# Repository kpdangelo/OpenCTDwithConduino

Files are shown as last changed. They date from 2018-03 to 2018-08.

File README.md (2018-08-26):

# OpenCTDwithConduino
OpenCTD with a low cost Conduino conductivity sensor

This has drift issues, see https://github.com/kpdangelo/OpenCTD-Conduino-K1.0 

*********************************************************************************************************************************************
This version is the basic design. During testing, a major drift in the reading was discovered. Two revisions were made, with some improvement. Continuing research is being done on Version 3 - see a separate entry for that, OpenCTDwithConduinoV3.
*********************************************************************************************************************************************

This project merges the Oceanography for Everyone Open CTD with the Conduino conductivity sensor.

Open CTD:
https://github.com/OceanographyforEveryone/OpenCTD

Conduino:
Marco Carminati, Paolo Luzzatto-Fegiz,
Conduino: Affordable and high-resolution multichannel water conductivity sensor using micro USB connectors,
In Sensors and Actuators B: Chemical, Volume 251, 2017, Pages 1034-1041, ISSN 0925-4005,
https://doi.org/10.1016/j.snb.2017.05.184.

Follow the basic assembly instructions from OpenCTD along with the included instructions for constructing
a Conduino.

PCBs can be ordered from OSHPARK, or Eagle and Gerber files are included here.

The system goes into a 2" PVC pipe and seals with Marine Epoxy and a 3D printed plug (file included here). 
See Conduino Pipe Assembly.pdf file.

First test was taking it into the surf and turbulence here at Spanish Bay for a few minutes, see excel file for that gem.

March 25, 2018

3/27/18
slight modification to the schematic to take away the filter on the network analyzer buffer (C5 and R3). It was giving a gigantic time constant to the measurement.

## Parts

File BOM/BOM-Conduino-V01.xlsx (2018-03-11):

Conduino Partslist
PCB can be ordered directly from OSHPARK
Part | Value | Device | Package | Description | Cost (single) | link
C1 | 1uF | CAP0603-CAP | 0603-CAP | Capacitor | $0.22 | https://www.digikey.com/product-detail/en/murata-electronics-north-america/GRM21BR61E106KA73L/490-5523-1-ND/2334919
C4 | 1uF | CAP0603-CAP | 0603-CAP | Capacitor | $0.22
C5 | 10pF | CAP0603-CAP | 0603-CAP | Capacitor | $0.29 | https://www.digikey.com/product-detail/en/kemet/C0603C100J8GAC7867/399-14932-1-ND/7382481
C8 | 100nF | CAP0603-CAP | 0603-CAP | Capacitor | $0.38 | https://www.digikey.com/product-detail/en/avx-corporation/08051C104JAT2A/478-5780-1-ND/2136372
C9 | 10uF | CAP0603-CAP | 0603-CAP | Capacitor | $0.15 | https://www.digikey.com/product-detail/en/taiyo-yuden/LMK212BJ106KG-T/587-1300-1-ND/931077
C10 | 100nF | CAP0603-CAP | 0603-CAP | Capacitor | $0.38
C11 | 1uF | CAP0603-CAP | 0603-CAP | Capacitor | $0.22
C12 | 10uF | CAP0603-CAP | 0603-CAP | Capacitor | $0.15
C13 | 100nF | CAP0603-CAP | 0603-CAP | Capacitor | $0.38
C16 | 10uF | CAP0603-CAP | 0603-CAP | Capacitor | $0.15
C17 | 100nF | CAP0603-CAP | 0603-CAP | Capacitor | $0.38
J1 | USBA-SIDE | USBA-SIDE | USBA-SIDE | USB Port | $0.40 | https://www.digikey.com/product-detail/en/amphenol-commercial-products/UE27AC54100/UE27AC54100-ND/1972253
J2 | Connector | 1X04 Header |  | Connector |  | use 0.1 mil headers
J3 | Connector | 1X02 header |  | Connector
R3 | 150K | RESISTOR0603-RES | 0603-RES | 0.10% | $0.35 | https://www.digikey.com/product-detail/en/panasonic-electronic-components/ERA-3AEB154V/P150KDBCT-ND/1466104
R4 | 20K | RESISTOR0603-RES | 0603-RES | 0.10% | $0.39 | https://www.digikey.com/product-detail/en/yageo/RT0805BRD0720KL/YAG1823CT-ND/5139271
R7 | 180 | RESISTOR0603-RES | 0603-RES | 0.10% | $0.35 | https://www.digikey.com/product-detail/en/panasonic-electronic-components/ERA-3AEB181V/P180DBCT-ND/1466034
R9 | 1.6K | RESISTOR0603-RES | 0603-RES | 1% | $0.10 | https://www.digikey.com/product-detail/en/panasonic-electronic-components/ERJ-3EKF1601V/P1.60KHCT-ND/1746732
R10 | 20K | RESISTOR0603-RES | 0603-RES | 0.10% | $0.39
U1 | AD5933SSOP-16-AD | AD5933SSOP-16-AD | SSOP-16-AD | Network Analyzer | $36.32 | https://www.digikey.com/product-detail/en/analog-devices-inc/AD5933YRSZ/AD5933YRSZ-ND/756602
U2 | AD4891-2 | AD4891-2 | SOIC_N | Op Amps | $2.09 | https://www.digikey.com/product-detail/en/analog-devices-inc/ADA4891-2ARZ/ADA4891-2ARZ-ND/2342638
U3 | ADR440A | ADR440A | SOIC_N | Voltage Reference | $6.32 | https://www.digikey.com/product-detail/en/analog-devices-inc/ADR440ARZ/ADR440ARZ-ND/1218276
PCB |  |  |  | Conduino PCB | $1.40 | https://www.oshpark.com/shared_projects/yAFaZZxk
 |  |  |  |  | $51.03

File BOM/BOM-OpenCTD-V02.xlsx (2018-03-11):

Open CTD with Conduino Partslist
Part | Value | Device | Package | Description | Cost (single)
JP1 | M031X03_NO_SILK | 1X03_NO_SILK | Header | Temp Sensor
JP2 | M031X03_NO_SILK | 1X03_NO_SILK | Header | Temp Sensor
JP3 | M031X03_NO_SILK | 1X03_NO_SILK | Header | Temp Sensor
JP4 | M041X04_NO_SILK | 1X04_NO_SILK | Header | Pressure Sensor
R1 | 4.7K | RESISTORPTH-1/4W | AXIAL-0.4 | Resistor
U1 | QDUINO_MINI | QDUINO_MINI | QDUINO_MINI |  | $29.95 | https://www.sparkfun.com/search/results?term=qduino
U2 | CONDUINO-V01 | CONDUINO-V01 | CONDUINO-V01 |  | $51.03
U3 | SD-CARD-READER-MICRO | SD-CARD-READER-MICRO | MICROSD_MOLEX |  | $1.11 | https://www.digikey.com/product-detail/en/molex-llc/0472192001/WM6698CT-ND/3044147
 | 12-position header for Qduino |  |  |  | $0.81 | https://www.digikey.com/product-detail/en/sullins-connector-solutions/PPPC121LFBN-RC/S7045-ND/810184
 | 12-position header for Qduino |  |  |  | $0.81
 | 4-position header for Conduino |  |  |  | $0.47 | https://www.digikey.com/product-detail/en/sullins-connector-solutions/PPPC041LFBN-RC/S7037-ND/810176
 | 2-position header for Conduino |  |  |  | $0.33 | https://www.digikey.com/product-detail/en/sullins-connector-solutions/PPPC021LFBN-RC/S7035-ND/810174
 | Pressure Sensor |  |  |  | $16.58 | https://www.digikey.com/product-detail/en/te-connectivity-measurement-specialties/MS580314BA01-00/223-1626-5-ND/5277631
 | 3 temperature sensors |  |  |  | $8.98 | https://www.amazon.com/gp/product/B00Q9YBIJI/ref=oh_aui_search_detailpage?ie=UTF8&psc=1
 | PCB | order from OSHPARK 3 at a time ($24.80) |  |  | $8.26 | https://www.oshpark.com/shared_projects/Nnyqy5C8
 | 2 Ah battery |  |  |  | $17.41 | https://www.amazon.com/gp/product/B0137ITW46/ref=oh_aui_search_detailpage?ie=UTF8&psc=1
 | PCB for pressure sensor |  |  |  | $2.95 | https://www.sparkfun.com/products/13655
 |  |  |  |  | $138.69

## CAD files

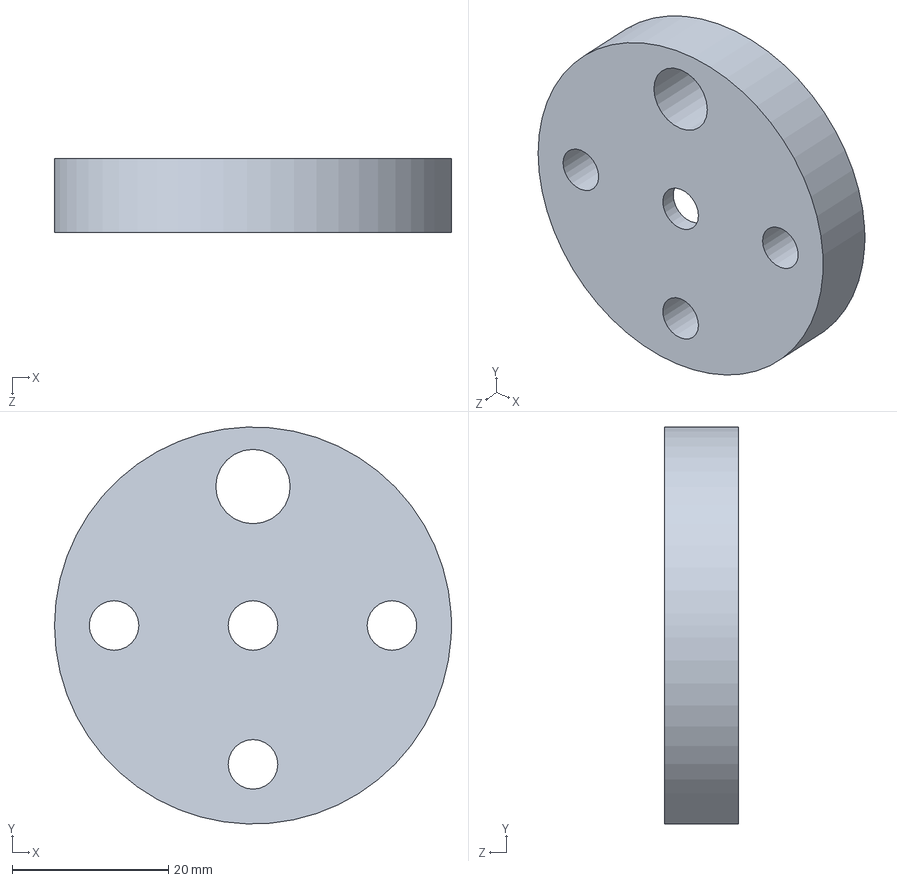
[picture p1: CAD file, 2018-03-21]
3D_Printer_Files/OpenCTD-Conduino-EndPlug.SLDPRT
50.8 x 50.8 x 9.53 mm

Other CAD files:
3D_Printer_Files/OpenCTD-Conduino-EndPlug.STL

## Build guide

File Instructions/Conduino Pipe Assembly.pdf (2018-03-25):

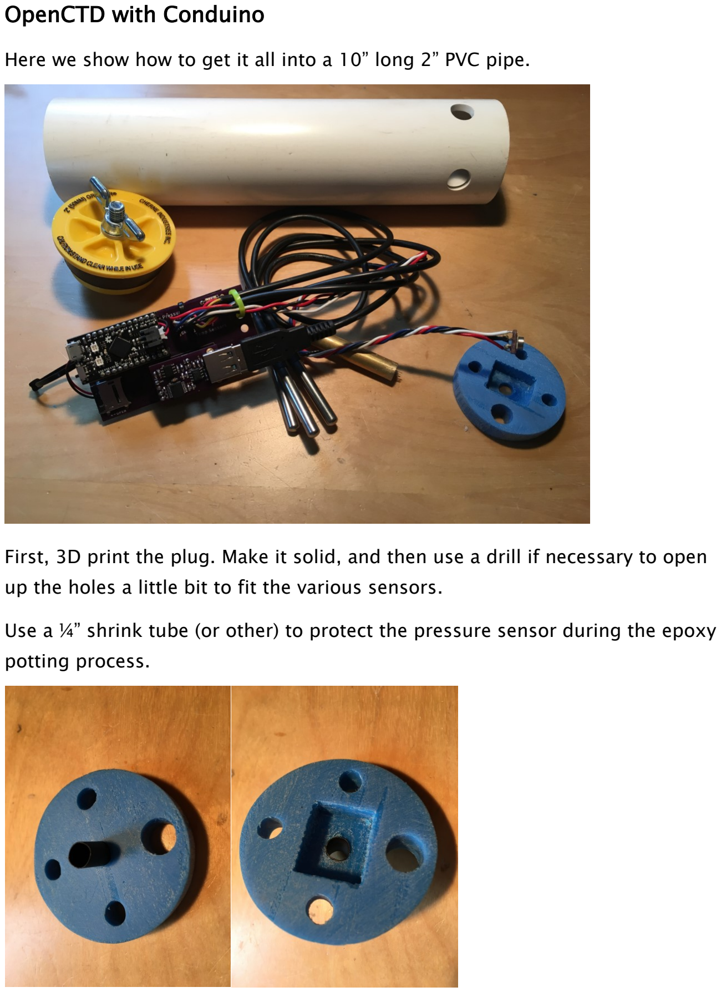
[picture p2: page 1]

OpenCTD with Conduino

Here we show how to get it all into a 10” long 2” PVC pipe.

First, 3D print the plug. Make it solid, and then use a drill if necessary to open up the holes a little bit to fit the various sensors.

Use a ¼” shrink tube (or other) to protect the pressure sensor during the epoxy potting process.

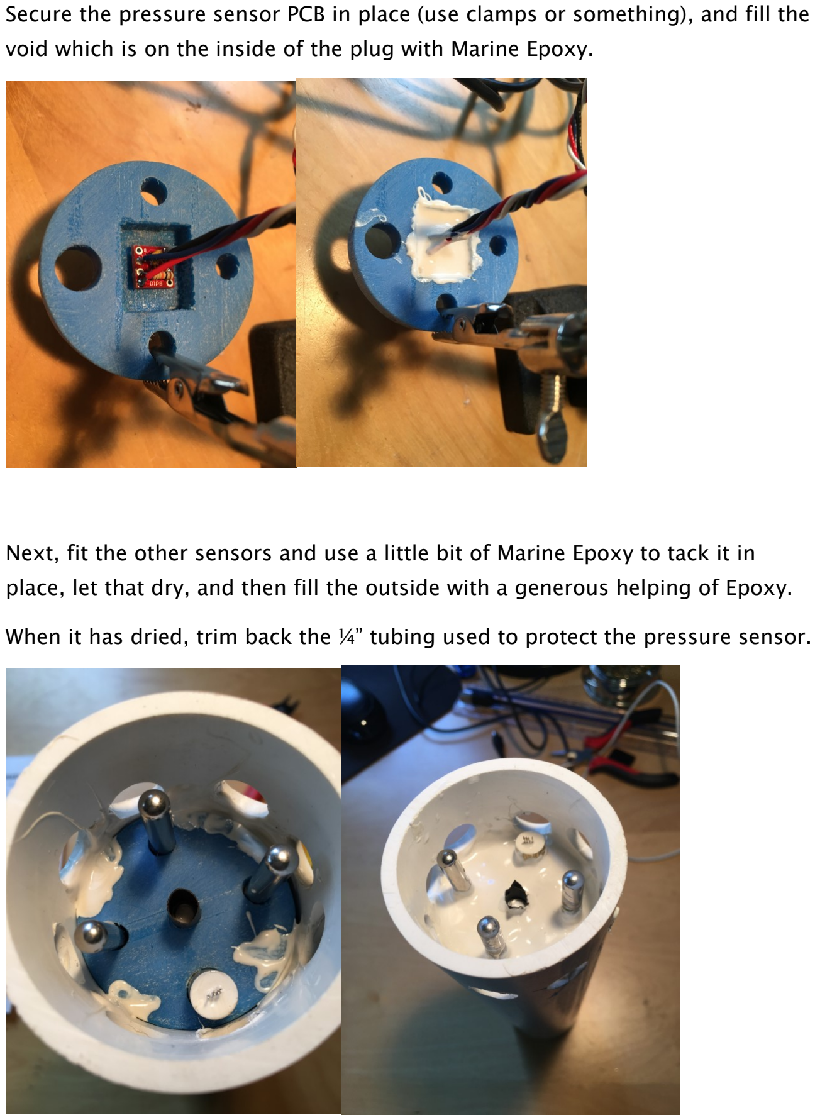
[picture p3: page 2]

Secure the pressure sensor PCB in place (use clamps or something), and fill the void which is on the inside of the plug with Marine Epoxy.

Next, fit the other sensors and use a little bit of Marine Epoxy to tack it in place, let that dry, and then fill the outside with a generous helping of Epoxy.

When it has dried, trim back the ¼” tubing used to protect the pressure sensor.

Cram the circuit board and the wires in the pipe. A twist of the circuit board is helpful. Attach the Gripper Plug and you’re ready to go. If you need it to sink, fill with mineral oil, or attach a weight.

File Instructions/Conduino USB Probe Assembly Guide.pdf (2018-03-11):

OpenCTD with Conduino

This version of the Open CTD instrument utilizes a Conduino conductivity probe made from a micro-USB cable.

https://github.com/OceanographyforEveryone/OpenCTD

Here’s a photo of the Conduino with three temperature sensors and calibration curve:

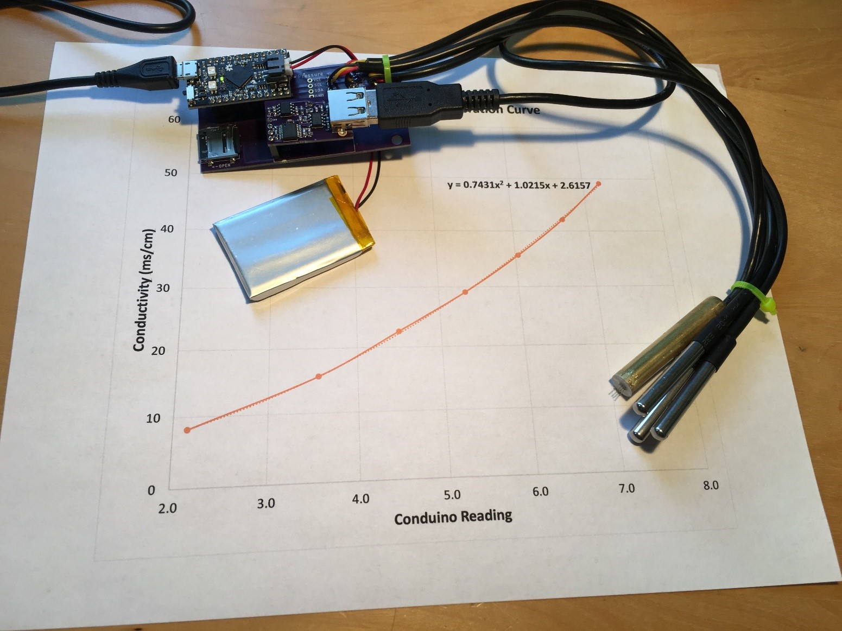
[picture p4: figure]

Conduino USB Probe Assembly Guide

Here’s one way to convert a micro-USB connector to a Conduino probe. Be patient and go slowly with the X-ACTO knife so the cable connections are preserved. A microscope is helpful.

First strip off the end of the cable housing by making a cut on all four sides.

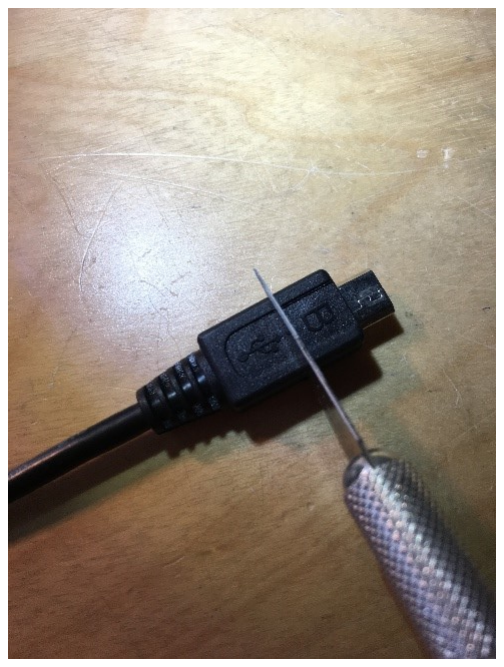
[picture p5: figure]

Cut again into fourths for ease of removal.

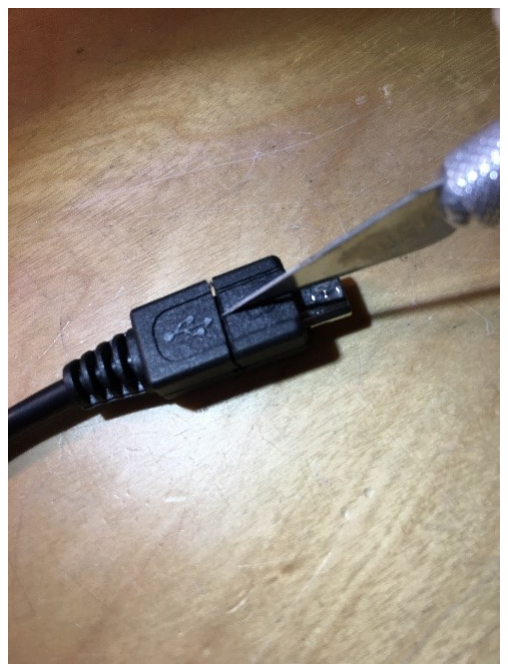
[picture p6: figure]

Remove the end of the housing and expose the connector.

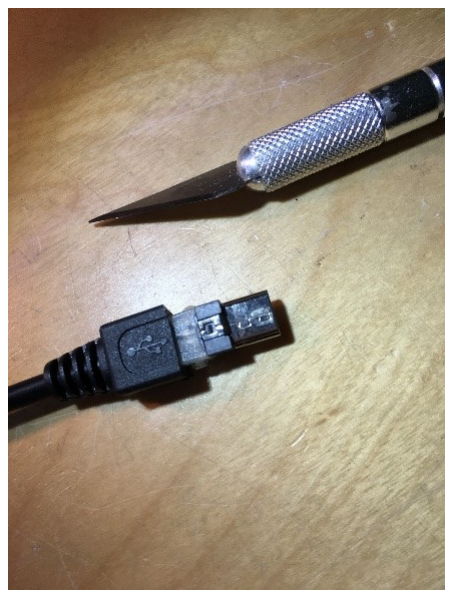
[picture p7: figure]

Peel back the clips on the four sides.

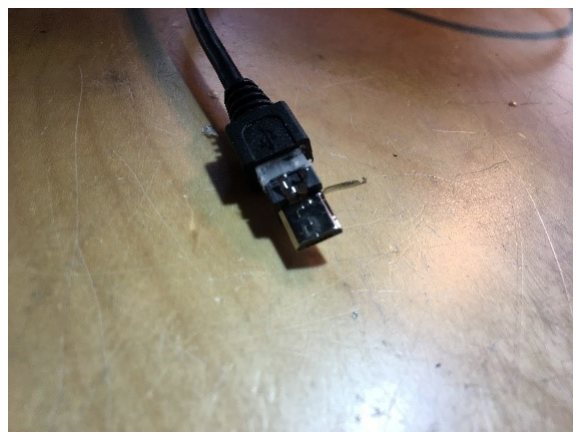
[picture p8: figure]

Carefully pull off the connector to reveal the electrodes. Darn, one of the electrodes came undone. Fortunately it’s the ID pin which is unused. The Conduino board uses D+ and D-.

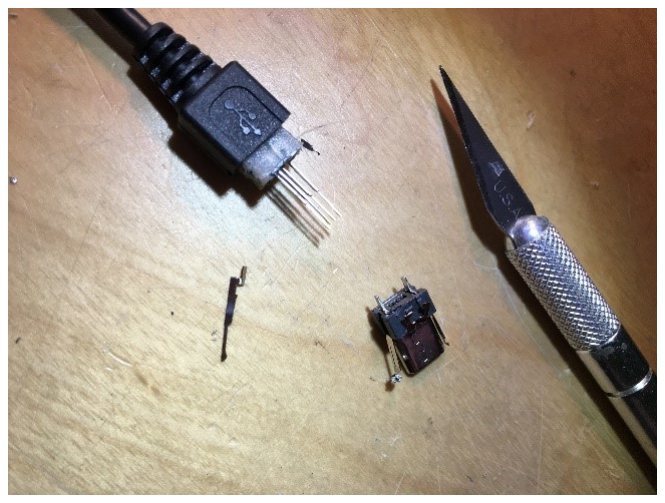
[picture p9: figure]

Now get rid of the rest of the housing so it can fit into a tube. Again, divide the housing into fourths by cutting down and slicing with the X-ACTO knife. Here’s all of the discarded stuff along with what remains of the cable we’ll use.

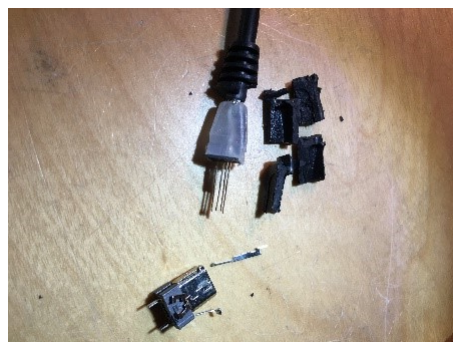
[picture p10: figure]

Use Marine Epoxy, readily available at Home Depot to cement the probe into a 3/8” tube. This tube is a brass tube because that’s what the local hardware store had.

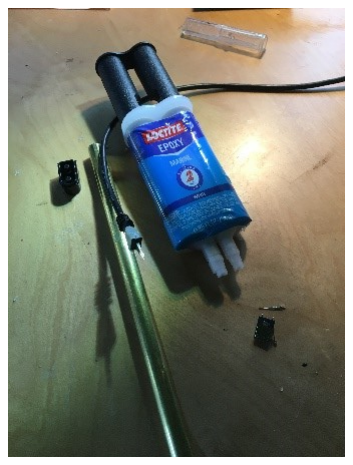
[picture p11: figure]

Use a holder to support the assembly while filling the void with epoxy. Here a Q-tip is used to mix and transport the epoxy.

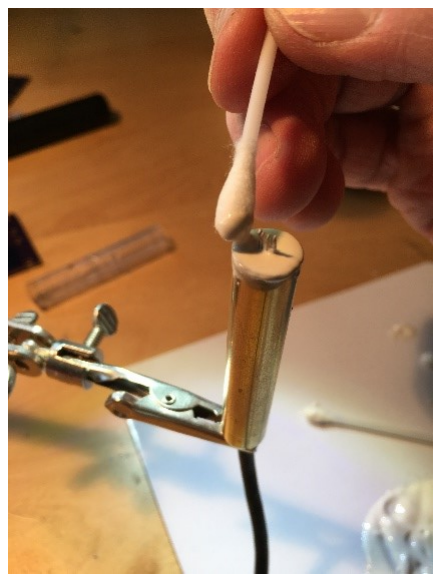
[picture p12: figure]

Use the X-ACTO knife to carefully clear away the excess stuck to the electrodes now. In about an hour after the epoxy has set, use a microscope and knife to clear away all of the excess epoxy. Then allow 24 hours or so to fully cure.

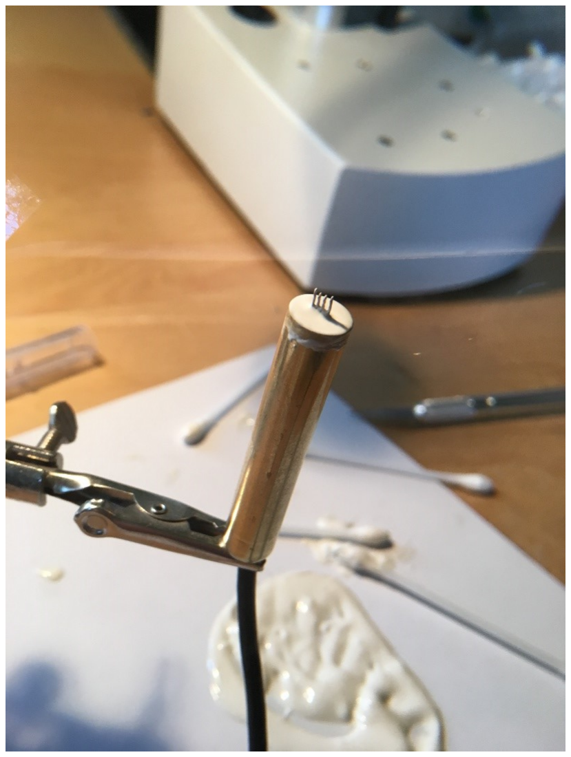
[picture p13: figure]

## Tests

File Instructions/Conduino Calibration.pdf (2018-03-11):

Conduino Calibration

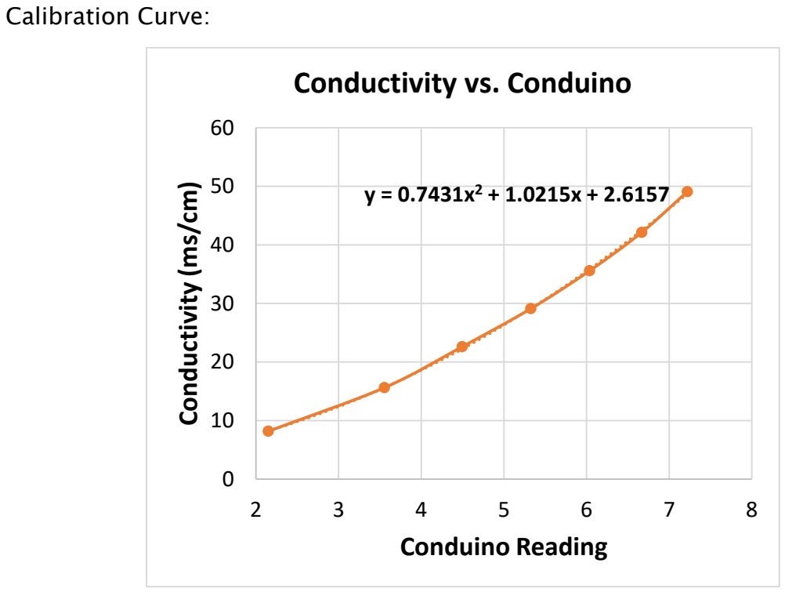
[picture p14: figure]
Calibration Curve:; Conductivity (ms/cm); Conduino Reading; Conductivity vs. Conduino

Seven known salinity samples were used to generate this curve: 5, 10, 15, 20, 25, 30 and 35 ppt salt concentration. To make the samples, weigh out half of the intended salt concentration (e.g. 2.5g, 5g, 7.5g etc.) and then add water to make the total weight 500g (or if you have a big vessel, go up to 1000g with the full salt weight).

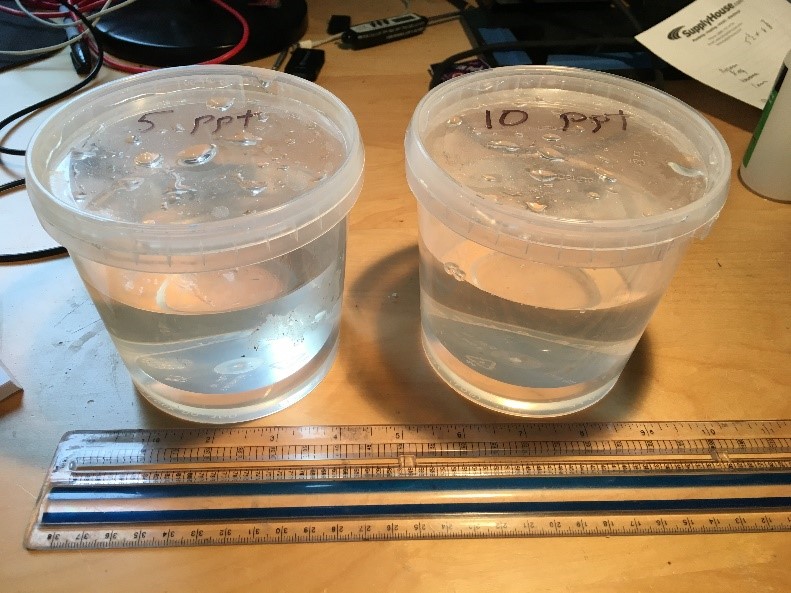
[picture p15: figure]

To take calibration measurements, use a temperature sensor along with the Conduino. Here, three temperature sensors were attached to the Conduino to be averaged during calibration. While constantly stirring the solution with the Conduino/Temperature sensor bundle, run the Arduino sketch and write the sensor values to the Arduino serial monitor. When the readings stabilize, cut a chunk of data and paste it into a txt file, and then import the txt file into Excel for averaging.

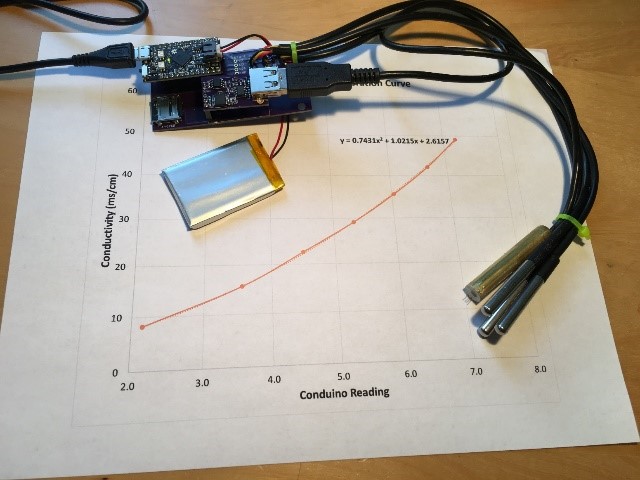
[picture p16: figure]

Use an online calculator to calculate a conductivity value based on temperature (sensed) and concentration (known):

http://salinometry.com/stp-conductivity-calculator/

Plot the data points for the 7 known samples as Conductivity vs. Conduino Reading. Add a trendline, in this case a polynomial, and add that to the sketch, or use it in a salinity calculating spreadsheet.

Data Sample:

Salinity (PPT) | t1 | t2 | t3 | Conduino Reading | Conductivity from salinometry.com | T average
5 | 20.56 | 20.60 | 20.62 | 2.150 | 8.171 | 20.59
10 | 20.75 | 20.81 | 20.87 | 3.554 | 15.608 | 20.81
15 | 20.65 | 20.69 | 20.75 | 4.494 | 22.598 | 20.70
20 | 20.23 | 20.25 | 20.31 | 5.326 | 29.100 | 20.26
25 | 20.14 | 20.19 | 20.25 | 6.036 | 35.572 | 20.19
30 | 20.37 | 20.44 | 20.45 | 6.667 | 42.122 | 20.42
35 | 21.12 | 21.15 | 21.19 | 7.220 | 49.090 | 21.15

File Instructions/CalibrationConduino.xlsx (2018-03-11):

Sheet: Sheet1
 | Conductivity calculators:
 | http://www.fivecreeks.org/monitor/sal.shtml
 | http://salinometry.com/stp-conductivity-calculator/
 | Polynomial Coefficients
 | 0.7431
 | 1.0215
 | 2.6157
data taken while constantly stirring known solutions
Salinity (PPT) | t1 | t2 | t3 | Conduino | ppt known Solutions | Conductivity from salinometry.com | T average | t1 | t2 | t3 | Conductivity polynomial calculation | *1000 | Salinity ppt calculated | Error
5 | 20.56 | 20.60 | 20.62 | 2.150 | 5 | 8.171 | 20.59 | 20.56 | 20.60 | 20.62 | 8.247 | 8247.087481 | 5.05 | 1.04%
10 | 20.75 | 20.81 | 20.87 | 3.554 | 10 | 15.608 | 20.81 | 20.75 | 20.81 | 20.87 | 15.630 | 15629.79149 | 10.02 | 0.20%
15 | 20.65 | 20.69 | 20.75 | 4.494 | 15 | 22.598 | 20.70 | 20.65 | 20.69 | 20.75 | 22.212 | 22212.3194 | 14.73 | -1.81%
20 | 20.23 | 20.25 | 20.31 | 5.326 | 20 | 29.100 | 20.26 | 20.23 | 20.25 | 20.31 | 29.135 | 29135.02113 | 20.03 | 0.16%
25 | 20.14 | 20.19 | 20.25 | 6.036 | 25 | 35.572 | 20.19 | 20.14 | 20.19 | 20.25 | 35.860 | 35859.64658 | 25.23 | 0.94%
30 | 20.37 | 20.44 | 20.45 | 6.667 | 30 | 42.122 | 20.42 | 20.37 | 20.44 | 20.45 | 42.455 | 42454.98524 | 30.28 | 0.93%
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

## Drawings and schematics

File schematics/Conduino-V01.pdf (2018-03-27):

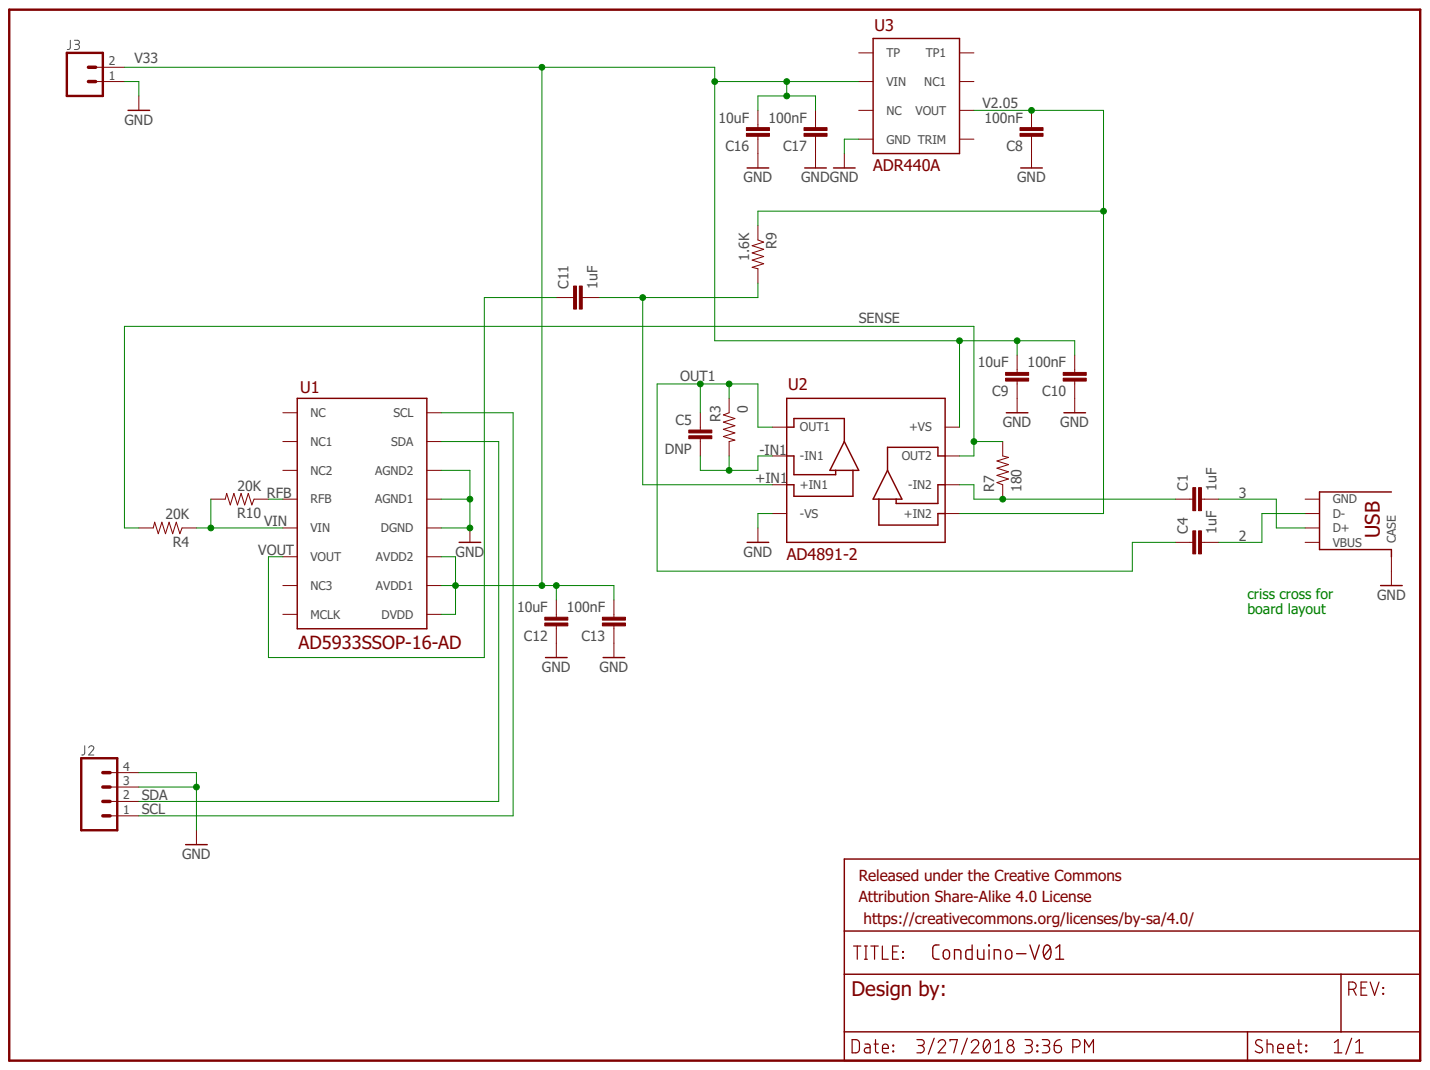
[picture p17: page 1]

criss cross for board layout

Released under the Creative Commons Attribution Share-Alike 4.0 License https://creativecommons.org/licenses/by-sa/4.0/

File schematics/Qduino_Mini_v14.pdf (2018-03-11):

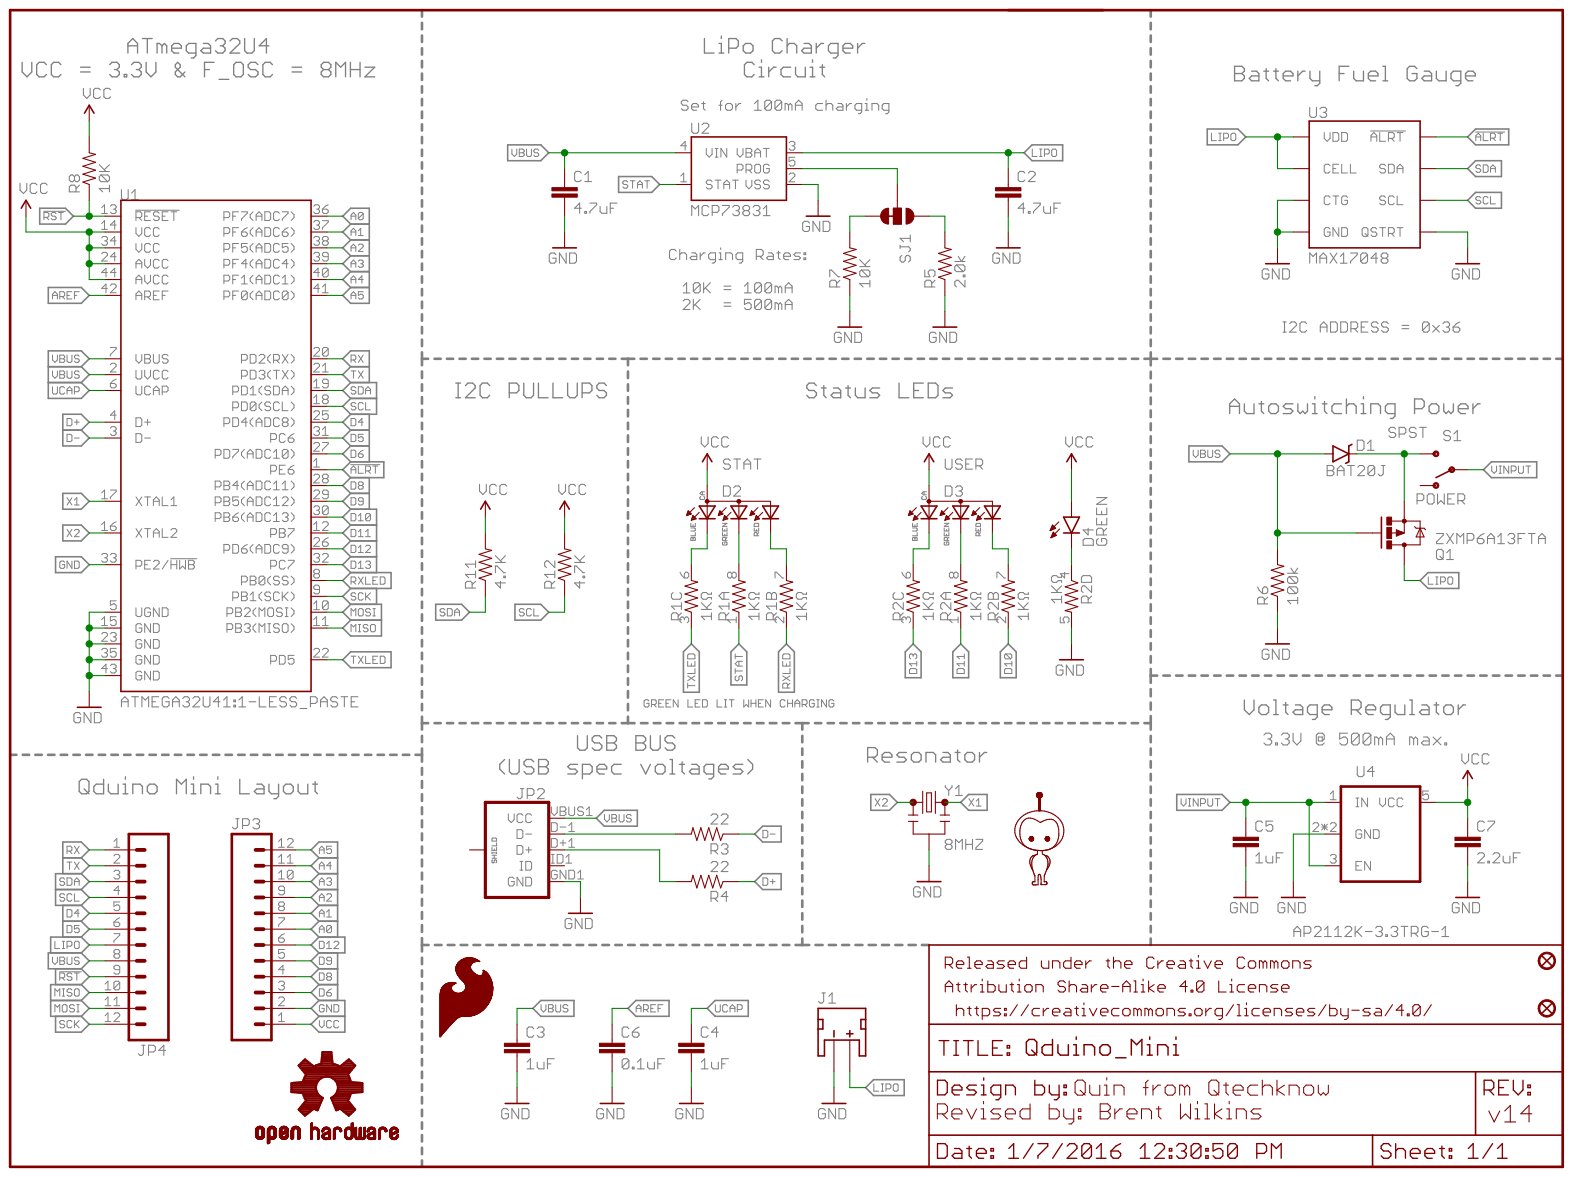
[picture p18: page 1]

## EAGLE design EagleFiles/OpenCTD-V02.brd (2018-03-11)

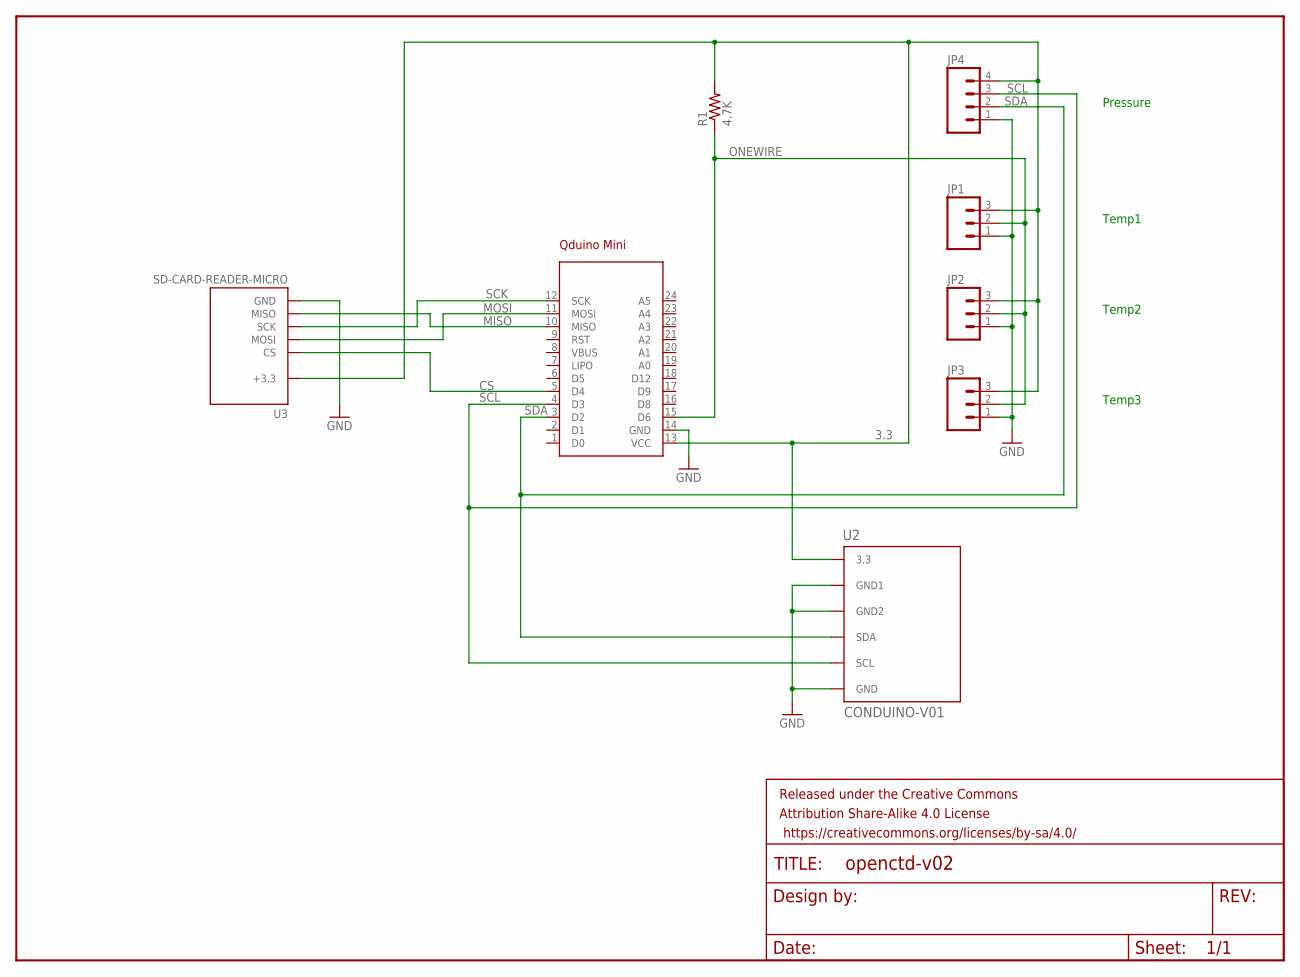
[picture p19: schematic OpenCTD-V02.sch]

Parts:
FRAME1: FRAME-LETTER; CREATIVE_COMMONS
JP1, JP2, JP3: M031X03_NO_SILK; 1X03_NO_SILK
JP4: M041X04_NO_SILK; 1X04_NO_SILK
R1: 4.7K; AXIAL-0.4
U1: QDUINO_MINI
U2: CONDUINO-V01
U3: SD-CARD-READER-MICRO; MICROSD_MOLEX

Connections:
3.3: JP1.3, JP2.3, JP3.3, JP4.4, R1.P$2 (2), U1.13 (VCC), U2.6 (3.3), U3.P$4 (+3.3)
CS: U1.5 (D4), U3.P$2 (CS)
GND: JP1.1, JP2.1, JP3.1, JP4.1, U1.14 (GND), U2.3 (GND), U2.4 (GND1), U2.5 (GND2), U3.P$6 (GND), U3.P$9 (GND), U3.P$10 (GND), U3.P$11 (GND), U3.P$12 (GND)
MISO: U1.10 (MISO), U3.P$7 (MISO)
MOSI: U1.11 (MOSI), U3.P$3 (MOSI)
ONEWIRE: JP1.2, JP2.2, JP3.2, R1.P$1 (1), U1.15 (D6)
SCK: U1.12 (SCK), U3.P$5 (SCK)
SCL: JP4.3, U1.4 (D3), U2.1 (SCL)
SDA: JP4.2, U1.3 (D2), U2.2 (SDA)

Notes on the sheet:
Pressure
Temp1
Temp2
Temp3

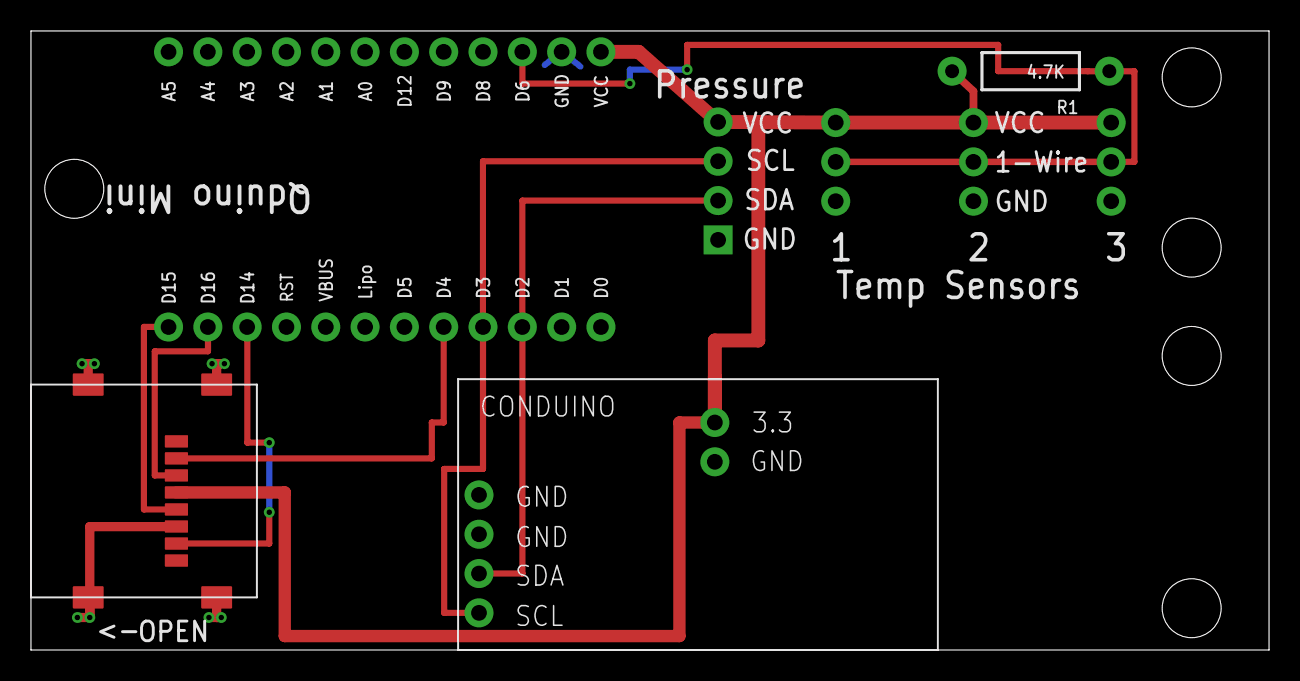
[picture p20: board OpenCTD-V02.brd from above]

Board: 2 copper layers, 80.0 x 40.0 mm, 9 parts (0 on the bottom side), 9 nets.

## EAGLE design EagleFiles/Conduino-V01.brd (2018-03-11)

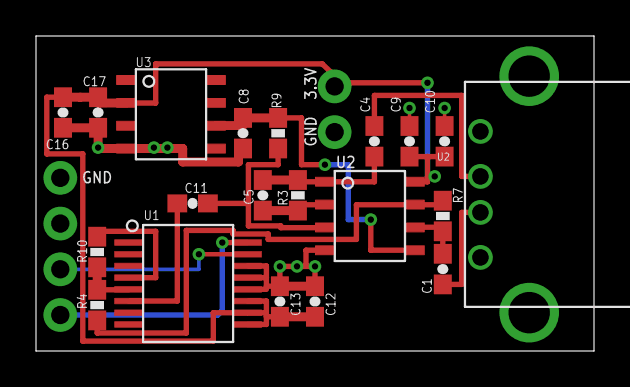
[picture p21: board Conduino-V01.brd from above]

Board: 2 copper layers, 31.0 x 17.5 mm, 23 parts (0 on the bottom side), 15 nets.

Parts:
C1, C4, C11: 1uF; 0603-CAP
C5: 10pF; 0603-CAP
C8, C10, C13, C17: 100nF; 0603-CAP
C9, C12, C16: 10uF; 0603-CAP
FRAME1: FRAME-LETTER; CREATIVE_COMMONS
J1: USBA-SIDE
J2: 1X04_NO_SILK
J3: 1X02_NO_SILK
R3: 150K; 0603-RES
R4, R10: 20K; 0603-RES
R7: 180; 0603-RES
R9: 1.6K; 0603-RES
U1: AD5933SSOP-16-AD; SSOP-16-AD
U2: AD4891-2; SOIC_N
U3: ADR440A; SOIC_N

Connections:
2: C4.2, J1.P$2
3: C1.2, J1.P$3
+IN1: C11.2, R9.2, U2.P$3
-IN1: C5.2, R3.2, U2.P$2
-IN2: C1.1, R7.1, U2.P$6
GND: C8.1, C9.1, C10.1, C12.1, C13.1, C16.1, C17.1, J1.P$5, J1.P$6, J2.3, J2.4, J3.1, U1.P$12, U1.P$13, U1.P$14, U2.P$4, U3.P$4
OUT1: C4.1, C5.1, R3.1, U2.P$1
RFB: R10.1, U1.P$4
SCL: J2.1, U1.P$16
SDA: J2.2, U1.P$15
SENSE: R4.2, R7.2, U2.P$7
V2.05: C8.2, R9.1, U2.P$5, U3.P$6
V33: C9.2, C10.2, C12.2, C13.2, C16.2, C17.2, J3.2, U1.P$9, U1.P$10, U1.P$11, U2.P$8, U3.P$2
VIN: R4.1, R10.2, U1.P$5
VOUT: C11.1, U1.P$6

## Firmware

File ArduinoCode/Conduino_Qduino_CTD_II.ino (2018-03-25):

///////////////////////////////////////////////////////////////////////////////////////////////////////////////
/*
 * Conduino_Qduino_CTD_II
 * 
   This sketch is adapted from the open CTD from Oceanography for Everyone
   http://www.oceanographyforeveryone.com/
   https://github.com/OceanographyforEveryone/OpenCTD

   Sensors are
   MS5803 pressure sensor
   Dallas 1-wire temperature sensors
   Conduino conductivity sensor which uses the AD5933 Network Analyzer

   Marco Carminati, Paolo Luzzatto-Fegiz,
   Conduino: Affordable and high-resolution multichannel water conductivity sensor using micro USB connectors,
   In Sensors and Actuators B: Chemical, Volume 251, 2017, Pages 1034-1041, ISSN 0925-4005,
   https://doi.org/10.1016/j.snb.2017.05.184.

   output format on SD card:
   TimeStamp(seconds) Pressure(atm) Temperature 1 2 3 (deg C) Conductivity (us/cm)

   Kevin D'Angelo
   3/25/18
*/
/////////////////////////////////////////////////////////////////////////////////////////////////////////////////
#include <Wire.h>
#include "Qduino.h"
qduino q;
#include <MS5803_14.h>
#include <avr/wdt.h>      // watch dog timer
///////////////////////////////////////////////////////////////////////////////////////////////
//  Sample Interval
//  loop takes about 810ms, so the sample interval needs to be greater than that.
//  The bulk of the time, 622ms, is used to communicate with the 1-wire temperature sensors.
//  watch dog timer is continuously reset while waiting for sample interval.
////////////////////////////////////////////////////////////////////////////////////////////////
#define SampleInterval 1000      // 1000 ms
///////////////////////////////////////////////////////////////////////////////////////////////////////////////
// Temperature and pressure releated
///////////////////////////////////////////////////////////////////////////////////////////////////////////////
//OneWire is used to get data from both temperature and conductivity sensors
#include <OneWire.h>  //CAN WE MAKE THIS LIBRARY SMALLER?

//DallasTemperature is used to query the temeprature sensors
#include <DallasTemperature.h>   //CAN WE MAKE THIS LIBRARY SMALLER?

// For the SD card reader.
#include <SPI.h>
#include <SD.h>

// Declare global variables.
float tempA;
float tempB;
float tempC;

OneWire oneWire(6);        // Define the OneWire port for temperature.
DallasTemperature sensors(&oneWire);  // Define DallasTemperature input based on OneWire.

MS_5803 sensor = MS_5803(4096);     // pressure sensor
double pressure_abs; // define absolute pressure variable.

/////////////////////////////////////////////////////////////////////////////////
//    CONDUINO RELATED
///////////////////////////////////////////////////////////////////////////////
// The user must calibrate the AD5933 system for a known impedance range to determine the gain factor

// polynomial coefficients for conversion from conduino reading to conductivity
// conductivity = CA*X^2 - CB*X + CC, where X is the conduino reading
#define CA 0.7431
#define CB 1.0215
#define CC 2.6157

#define AD5933_ADDR 0x0D
#define AD5245_ADDR 0x2D //B0101101; // << assumes AD0 tied to VCC

const float CLOCK_SPEED = 16.776 * pow(10, 6); // AD5933 has internal clock of 16.776 MHz

const int CONTROL_REGISTER[2] =                    { 0x80, 0x81       }; // see mapping below
const int START_FREQUENCY_REGISTER[3] =            { 0x82, 0x83, 0x84 }; // 24 bits for start frequency
const int FREQ_INCREMENT_REGISTER[3] =             { 0x85, 0x86, 0x87 }; // 24 bits for frequency increment
const int NUM_INCREMENTS_REGISTER[2] =             { 0x88, 0x89       }; //  9 bits for # of increments
const int NUM_SETTLING_CYCLES_REGISTER[2] =        { 0x8A, 0x8B       }; //  9 bits + 1 modifier for # of settling times
const int STATUS_REGISTER[1] =                     { 0x8F             }; // see mapping below
const int TEMPERATURE_DATA_REGISTER[2] =           { 0x92, 0x93       }; // 16-bit, twos complement format
const int REAL_DATA_REGISTER[2] =                  { 0x94, 0x95       }; // 16-bit, twos complement format
const int IMAG_DATA_REGISTER[2] =                  { 0x96, 0x97       }; // 16-bit, twos complement format

// control register map (D15 to D12)
const int DEFAULT_VALUE =                 B0000; // initial setting
const int INITIALIZE =                    B0001; // excite the unknown impedance initially
const int START_SWEEP =                   B0010; // begin the frequency sweep
const int INCREMENT =                     B0011; // step to the next frequency point
const int REPEAT =                        B0100; // repeat the current frequency point measurement
const int MEASURE_TEMP =                  B1001; // initiates a temperature reading
const int POWER_DOWN =                    B1010; // VOUT and VIN are connected internally to ground
const int STANDBY =                       B1011; // VOUT and VIN are connected internally to ground

const int BLOCK_WRITE = B1010000;
const int BLOCK_READ =  B1010001;
const int ADDRESS_PTR = 0xB0;// B1011000;

const int validTemperatureMeasurement =  1;
const int validImpedanceData =           2;
const int frequencySweepComplete =       4;

//functions declarations
int checkStatus();
boolean measureTemperature();
byte frequencyCode(float, int);
boolean setStartFrequency(float);
boolean setFrequencyIncrement(float);
boolean setNumberOfIncrements(int);
boolean setNumberOfSettlingTimes(int);
void configureAD5933(int, float, float, int);
int getByte(int);
boolean setByte(int, int);
boolean setControlRegister(int);

boolean setControlRegister2();

int reading = 0;
byte rxByte;
int number;
char FirstChar[1];
char SecondChar[1];

int e = 0;
int y;
int ch;
int u;
int real;
int imag ;

long timeStamp;
long time1;

void setup() {
  Wire.begin();
  Serial.begin(9600);
  wdt_enable(WDTO_2S);      // 2 second watch dog timer reset interval
  q.setup();

  pinMode(8, OUTPUT);   // use for scope timing measurements

  if (!SD.begin(4)) {
    Serial.println("Card failed");  // Log to serial monitor if SD card doesn't work.
    q.setRGB(RED);    // SD card bad, turn on the red light
    return;
  }
  else {          // SD card is good, turn on the green light for 1 second
    q.setRGB(GREEN);
    delay(1000);
    q.ledOff();
  }
  
  wdt_reset();      // pet the dog

  sensors.begin();    // Initialize the temperature sensors
  sensor.initializeMS_5803();   // Initialize pressure sensor

  configureAD5933(2, // Conduino network analyzer, number of settling times
                  1 * pow(10, 5), // start frequency (Hz)
                  1 * pow(10, 4), // frequency increment (Hz)
                  0); // number of increments

  setControlRegister2();

  //0.Inizialize bit D11,D10,D9,D8
  setControlRegister2();

  // 1. place AD5933 in standby mode
  setControlRegister(STANDBY);

  // 2. initialize with start frequency
  setControlRegister(INITIALIZE);

  // 3. start frequency sweep
  setControlRegister(START_SWEEP);

  real = getByte(REAL_DATA_REGISTER[0]) << 8;
  real |= getByte(REAL_DATA_REGISTER[1]);

  imag = getByte(IMAG_DATA_REGISTER[0]) << 8;
  imag |= getByte(IMAG_DATA_REGISTER[1]);

  time1 = millis();     // initialize time stamp
}

void loop() {

  timeStamp += millis() - time1;
  time1 = millis();

  digitalWrite (8, HIGH);   // for scope measurement of time to sample all sensors
  sensor.readSensor();    // read pressure sensor, takes 22ms

  // Read temperature sensors.
  sensors.requestTemperatures();    // takes 622 ms
  tempA = sensors.getTempCByIndex(0);
  tempB = sensors.getTempCByIndex(1);
  tempC = sensors.getTempCByIndex(2); // takes 126ms

  setControlRegister(REPEAT);     // takes 38ms for Conduino reading
  delay(6);

  // 5. read Conduino values
  real = getByte(REAL_DATA_REGISTER[0]) << 8;
  real |= getByte(REAL_DATA_REGISTER[1]);

  if (real > 0x7FFF) { // negative value
    real &= 0x7FFF;
    real -= 0x10000;
  }

  imag = getByte(IMAG_DATA_REGISTER[0]) << 8;
  imag |= getByte(IMAG_DATA_REGISTER[1]);

  if (imag > 0x7FFF) { // negative value
    imag &= 0x7FFF;
    imag -= 0x10000;
  }
  // Conduino Calculations
  double magnitude = sqrt(pow(double(real), 2) + pow(double(imag), 2));
  double gain = 2.3 * pow(10, -10); //calibrated with 220kOhm resistor on 1/3/12

  double impedance = 1 / (3.5 * gain * magnitude * 45400 / 1.63);

  double phase = atan(double(imag) / double(real)) * 360 / (2 * 3.14) + 47;

  double ConduinoReading = 129 / impedance;  // K=129/m

  // Polynomial Conductivity Calculation (coefficients will be different for each Conduino)
  double Conductivity = CA * ConduinoReading * ConduinoReading + CB * ConduinoReading + CC; // ms/mm
  Conductivity = Conductivity * 1000;  // ms/m

  File dataFile = SD.open("datalog.txt", FILE_WRITE);   // takes ~4ms
  if (dataFile) {
    dataFile.print(timeStamp / 1000.0); dataFile.print(" ");
    dataFile.print(sensor.pressure()); dataFile.print(" ");
    dataFile.print(tempA); dataFile.print(" ");
    dataFile.print(tempB); dataFile.print(" ");
    dataFile.print(tempC); dataFile.print(" ");
    dataFile.println(Conductivity);
    dataFile.close();
  }

  //    Write to serial monitor or not Comment/Uncomment
  //  Serial.print(timeStamp / 1000.0); Serial.print(" ");
  //  Serial.print (sensor.pressure()); Serial.print(" ");
  //  Serial.print (tempA); Serial.print(" ");
  //  Serial.print (tempB); Serial.print (" ");
  //  Serial.print (tempC); Serial.print (" ");
  //  Serial.println(Conductivity);

  digitalWrite(8, LOW);   // scope measurement end (about 810ms)
  while (millis() - time1 < SampleInterval) { // wait for Sample Interval
    wdt_reset();              // reset the watchdog timer in case SampleInterval > 2000
  }

}
////////////////////////////////////////////////////////////////////////
//  Conduino Related Subroutines
////////////////////////////////////////////////////////////////////////
// message sequence:
// to set the memory address:
// 1. slave address
// 2. pointer command
// 3. register address to point to

// to write data (address already set):
// 1. slave address
// 2. block write
// 3. number bytes write
// 4. byte 0, byte 1, byte 2, etc.

// to read data (address is already set):
// 1. slave address with read bit high
// 2. register data is returned

// to read a block of data (address is already set):
// 1. slave address
// 2. block read
// 3. number of bytes
// 4. slave address (read bit high)
// 5. byte 0, byte 1, byte 2, etc.

// control register map (D10 to D9)
// ranges = {2.0 V p-p, 200 mV p-p, 400 mV p-p, 1.0 V p-p}
const int OUTPUT_VOLTAGE[4] = {
  B00, B01, B10, B11
};

// control register map (D11, D8 to D0)
// D11 = no operation
// D8 = PGA gain (0 = x5, 1 = x1) // amplifies the response signal into the ADC
// D7 = reserved, set to 0
// D6 = reserved, set to 0
// D5 = reserved, set to 0
// D4 = reset // interrupts a frequency sweep
// D3 = external system clock, set to 1; internal system clock, set to 0
// D2 = reserved, set to 0
// D1 = reserved, set to 0
// D0 = reserved, set to 0

// number of increments register
// 0x88: D15 to D9 -- don't care
// 0x89: D8 -- number of increments bit 1
// 0x89: D7 to D0 -- number of increments bits 2 through 9; 9-bit integer number stored in binary format

// number of settling times
// 0x8A: D15 to D11 -- don't care
// 0x8A: D10 to D9 -- 2-bit decode
//        0 0 = default
//        0 1 = # of cycles x 2
//        1 0 = reserved
//        1 1 = # of cycles x 4
// 0x8A: D8 -- MSB number of settling times
// 0x8B: D7 to D0 -- number of settling times; 9-bit integer number stored in binary format

// status register

int checkStatus() {
  return (getByte(STATUS_REGISTER[0]) & 7);
}
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

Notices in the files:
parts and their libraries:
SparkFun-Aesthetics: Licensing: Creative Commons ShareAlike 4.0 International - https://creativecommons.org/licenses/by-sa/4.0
